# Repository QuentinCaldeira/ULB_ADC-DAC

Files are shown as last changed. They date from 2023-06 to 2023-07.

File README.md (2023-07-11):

# ULB_ADC-DAC

Ce git contient tout les documents liés à la conception de la carte de protection des calculateurs analogiques ADC/DAC.
Dans ce git, vous pouvez trouver :

## Datasheets

Ce répertoire contient toutes les **datasheets** et **notes d'application** qui ont étés utilisées dans la conception dde ce projet.

## Documentation PCB

Ce répertoire contient tout les fichiers de conception du PCB pour le logiciel KiCAD. Des images de la carte et du schematic ont aussi été mis à disposition.

## Gravure

Ce répertoire contient principalement le fichier `.svg` qui à été utilisé pour graver la face avant de la carte, ainsi qu'un template **à l'échelle** pour le gabarit 8x5.

## LaTeX

Ce répertoire contient tout les fichiers liés à la compilation LaTeX du fichier `Documenation.pdf`. Il y a toutes les images liées au document, le template global, les logos, etc...

## Tuto

Ce répertoire contient des tutoriels écrits en `markdown`. Ces tutoriels ont été écrits lorsque j'ai rencontré des difficultés à faire une tâche.

## 3D

Ce répertoire contient les fichiers 3D FreeCAD et `.stl` pour imprimer les pièces permettant de visser la face avant au PCB.

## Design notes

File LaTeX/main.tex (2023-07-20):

\documentclass{report}
\usepackage{quentin}
\definecolor{mycolor}{HTML}{00519d}
\definecolor{darkWhite}{rgb}{0.94,0.94,0.94}
\usepackage{enumitem}
%\usepackage{luacode,numprint,fourier}
\usepackage{hyperref}
\usepackage{pgfplots}
\usepackage{mathtools}
\usepackage{graphicx}
\usepackage{pdfpages}
\usepackage[backend=biber]{biblatex} %backend tells biblatex what you will be using to process the bibliography file
\addbibresource{bib.bib}

\AddToShipoutPicture*{
\begin{tikzpicture}[remember picture, overlay]

\draw[fill=mycolor!50,draw=mycolor!50](current page.north west)rectangle([yshift=-\paperheight/24]current page.north east);
\draw[draw=mycolor!60, line width=1.5mm]([yshift=-\paperheight/24]current page.north west)--([yshift=-\paperheight/24]current page.north east);

\draw[fill=mycolor!50,draw=mycolor!50](current page.south west)rectangle([yshift=\paperheight/24]current page.south east);
\draw[draw=mycolor!60, line width=1.5mm]([yshift=\paperheight/24]current page.south west)--([yshift=\paperheight/24]current page.south east);
\end{tikzpicture}
}

\begin{document}

\titre{
\Huge\textbf{Documentation des cartes de protections}\\[0.2cm]
\large\textbf{Pour le calculateur analogique}\\
\rule{\linewidth}{0.5mm}
\\[2cm]
\LARGE Quentin \textsc{Caldeira}
}

\tableofcontents
\thispagestyle{empty}
\entete
\newpage
\thispagestyle{empty}
\listoffigures
\entete
\listoftables
\entete

\chapter{Contexte}
\thispagestyle{empty}
La carte a pour objectif d'interfacer une face avant avec une carte d'acquisition. Son but est de protéger la carte de potentielles mauvaises manipulations. Étant donné le coût d'une carte d'acquisition, la carte de protection doit protéger la carte d'acquisition. Dans le pire des cas, il est préférable que ce soit la carte de protection qui soit détruite, plutôt que la carte d'acquisition. L'idéal reste qu'aucun des deux éléments ne soit détruit. On souhaite principalement se protéger des courts-circuits et de tensions trop élevées.Une première carte a été réalisée en 1993. Cette carte est fonctionnelle, mais présente quelques défauts qui seront explicités. Cette nouvelle carte a pour objectif de corriger les défauts de l'ancien modèle, de réduire le nombre d'entrées/sorties, et de donner un coup de jeune à la carte.

\chapter{Présentation de l'existant}
\thispagestyle{empty}
Cette partie détaillera les cartes précédemment installées dans le calculateur. La carte dispose de 20 entrées et 12 sorties. Il semblerait qu'elle ait été conçue ainsi afin d'utiliser toutes les broches inférieures du connecteur fond de panier. Le connecteur utilisé est un DIN 41612 de 64 broches. Il s'avère qu'au quotidien, seulement 8 entrées et 2 sorties sont utilisées au maximum. La carte mesure 10 cm de largeur et 22 cm de longueur. C'est une taille standard que toutes les cartes insérées dans les racks doivent respecter. Les connecteurs utilisés sur la face avant sont des connecteurs banane, de couleurs différentes en fonction d'une entrée, d'une sortie ou d'une masse. Il n'y a pas de détrompeur entre les 3 connectiques.

\section{Les cartes d'acquisition}
Les cartes d'acquisition précédemment utilisées étaient des NI PCI 6014 et NI PCI 6024E. Ces cartes sont au format PCI. Les spécifications de cette carte sont synthétisées dans le tableau ci-dessous.

\begin{center}
\begin{table}[h!]
\begin{tabular}{l|l|l|}
\cline{2-3}
                                                                 & Entrée                                 & Sortie                   \\ \hline
\multicolumn{1}{|l|}{Tension d'E/S max en fonctionnement normal} & $\pm 10 V$                             & $\pm 10 V$               \\ \hline
\multicolumn{1}{|l|}{Impédance d'entrée/sortie}                  & 100 G$\Omega$ en parallèle avec 100 pF & 0,1 G$\Omega$            \\ \hline
\multicolumn{1}{|l|}{Protection contre les tensions (On/Off)}    & 25 / 15 V                              & Court-circuit à la masse \\ \hline
\multicolumn{1}{|l|}{Courant de sortie max}                      & -                                      & 5 à 10 mA                \\ \hline
\multicolumn{1}{|l|}{Courant d'entrée max}                       & -                                      & 5 à -10 mA               \\ \hline
\end{tabular}
\caption{Spécifications des cartes PCI 6014 et PCI 6024E}
\end{table}
\end{center}

\section{Alimentation des amplificateurs}
Comme les amplificateurs utilisés sont alimentés en $\pm$15 V, et que les cartes ont une alimentation par défaut de $\pm$24 V, il a fallu adapter cette tension. Des régulateurs de tensions positifs et négatifs ont été utilisés. Un 7815CT a été utilisé pour générer la tension +15 V, et un 7915 pour la tension -15 V. Des capacités de filtrage ont été placés en amont et en aval des alimentations, ainsi que des diodes de protections servant à prévenir des inversions de polarité. La mise en place d'un tel circuit est explicité sur la \bsc{Figure} \ref{fig:alim_exist}. Le choix des capacités se fait souvent en fonction de la documentation du constructeur. De plus, des dissipateurs thermiques ont étés placé afin de limiter la chauffe des régulateurs de tension.

\newpage%%%%%%%%%%%%%%%%%%
\begin{figure}[!h]
\centering
\begin{circuitikz}
\ctikzset{multipoles/thickness=3}
\ctikzset{multipoles/dipchip/width=2}

\draw (0,0) node[dipchip,
num pins=6, hide numbers, no topmark,
external pins width=0](C){7815CT};
\node [right, font=\tiny] at (C.bpin 2) {Vin};
\node [left, font=\tiny] at (C.bpin 5) {Vout};
\draw (C.s)node[above,font=\tiny]{GND} -- ++(0,-1) node[ground]{};

\draw(C.bpin 2)to[empty diode,invert]++(-3,0)node[left]{+24 V};
\draw(C.bpin 2)--++(-.5,0)to[C,l_=22pF]++(0,-2);
\draw(C.bpin 5)--++(.5,0)to[C,l=22pF]++(0,-2)--++(-1.9,0)--++(-1.9,0);
\draw(C.bpin 5)--++(2,0)node[right]{+15 V};

\draw (0,-4) node[dipchip,
num pins=6, hide numbers, no topmark,
external pins width=0](C){7915};
\node [right, font=\tiny] at (C.bpin 2) {Vin};
\node [left, font=\tiny] at (C.bpin 5) {Vout};
\draw (C.s)node[above,font=\tiny]{GND} -- ++(0,-1) node[ground]{};

\draw(C.bpin 2)to[empty diode]++(-3,0)node[left]{-24 V};
\draw(C.bpin 2)--++(-.5,0)to[C,l_=22pF]++(0,-2);
\draw(C.bpin 5)--++(.5,0)to[C,l=22pF]++(0,-2)--++(-1.9,0)--++(-1.9,0);
\draw(C.bpin 5)--++(2,0)node[right]{-15 V};

\end{circuitikz}
\caption{Schéma de principe de protection de l'alimentation sur la carte existante}
\label{fig:alim_exist}
\end{figure}

\section{Protection des entrées}
\subsection{Présentation}

Afin de protéger les entrées, le montage sur la \bsc{Figure} \ref{fig:entree_exist} a été utilisé. Ce montage possède deux diodes Zener en tête-bêche afin d'écrêter la tension à $\pm$10 V. Une résistance de 1 M$\Omega$ est placée en entrée, ainsi qu'en contre-réaction. Une résistance de 1 k$\Omega$ est placée en sortie afin de limiter le courant. Comme la tension de sortie sera de maximum 10 V, le courant devrait être de maximum 10 mA. Le montage est de type \textbf{inverseur}, ce qui veut dire que le gain est d'environ \textbf{-1}. Une entrée à +10 V sera vue comme -10 V par la carte d'acquisition. Ce gain négatif est corrigé par le logiciel qui récupère les signaux (\bsc{MatLAB} en l'occurence). L'amplificateur opérationnel est monté sur un socket DIP-14, afin qu'il soit remplaçable facilement.

\begin{figure}[!h]
\centering
\begin{circuitikz}[european]
\ctikzset{resistors/scale=0.7, capacitors/scale=0.7, diodes/scale=0.7, inductors/scale=0.7}
\draw (0,0) node[op amp,scale=1] (opamp) {};
\draw (opamp.-) --++ (-.5,0)node(b){}--++(0,1)node(a){}to[name=r1,R,l=1M$\Omega$]++(3,0)--++(0,-1.49)node(c){} to (opamp.out);
\draw (a.south)--++(0,1)to[Zener diode]++(1.5,0)to[Zener diode,invert]++(1.5,0)--++(0,-1);
\draw (b.east)to[R,l=1M$\Omega$]++(-2,0)node[left]{Entrée};
\draw (c.west)to[R,l=1k$\Omega$]++(2,0)node[right]{Carte d'acquisition};
\draw (opamp.+)node[ground]{};
\draw (opamp.up) --++ (0,.2) node[above] {15 V};
\draw (opamp.down) --++ (0,-.2) node[below] {-15 V};
\end{circuitikz}
\caption{Schéma de principe de protection des entrées sur la carte existante}
\label{fig:entree_exist}
\end{figure}

\subsection{Mesures}
Pour les entrées, il n'y a pas trop de soucis de protection. En injectant 10 V en entrée, on récupère bien environ -10 V en sortie. Lorsqu'une tension d'alimentation telle que -15 V est injectée, la tension est bien limitée à environ 10 V.

\section{Protection des sorties}
\subsection{Présentation}

Afin de protéger les sorties, le montage sur la \bsc{Figure} \ref{fig:sortie_exist} a été utilisé. Ce montage possède un filtre passe-bas du 1$^{er}$ ordre. L'intérêt d'un tel filtre est discutable, car le signal provient de la carte d'acquisition. Un deuxième filtre passe-bas est placé dans la contre-réaction de l'amplificateur opérationnel. En sortie de ce montage, une résistance de 1 k$\Omega$ a été placée afin de limiter le courant en cas de court-circuits. Cette résistance pose problème car de manière générale, dans un circuit, on cherche à avoir une forte impédance d'entrée et une faible impédance de sortie. On cherche cela afin de faciliter les adaptations d'impédances, c'est-à-dire que la majorité des courants circulant dans un circuit n'ont pas d'impact sur l'autre circuit raccordé. Hors, il a été remarqué qu'avec cette résistance, une chute de tension est observée sur certains procédés.

\begin{figure}[!h]
\centering
\begin{circuitikz}[european]
\ctikzset{resistors/scale=0.7, capacitors/scale=0.7, diodes/scale=0.7, inductors/scale=0.7}
\draw (0,0) node[op amp,scale=1] (opamp) {};
\draw (opamp.-) --++ (-.5,0)node(b){}--++(0,1)node(a){}to[name=r1,R,l=1M$\Omega$]++(3,0)--++(0,-1.49)node(c){} to (opamp.out);
\draw (a.south)--++(0,1)to[C,l=22pF]++(3,0)--++(0,-1);
\draw (b.east)to[R,l=1M$\Omega$]++(-3,0)node[left]{Carte d'acquisition};
\draw (b.west)--++(-0.5,0)--++(0,-0.5)to[C,l=10nF]++(0,-0.5)node[ground]{};
\draw (c.west)to[R,l=1k$\Omega$]++(2,0)node[right]{Sortie};
\draw (opamp.+)node[ground]{};
\draw (opamp.up) --++ (0,.2) node[above] {15 V};
\draw (opamp.down) --++ (0,-.2) node[below] {-15 V};
\end{circuitikz}
\caption{Schéma de principe de protection des sorties sur la carte existante}
\label{fig:sortie_exist}
\end{figure}

\subsection{Mesures}
Pour la sortie, des mesures ont d'abord été faites pour estimer la chute de tension. Sur le procédé de régulation de température par exemple, pour une tension de 10 V fournie par la carte NI, nous ne récupérons que 9 V sur le procédé, soit une chute de 1 V pour 2 mA de consommation. La solution actuelle pour palier à ce problème est de passer par un deuxième amplificateur opérationnel qui a rôle de \textbf{buffer}, c'est-à-dire de faire le lien entre deux étages grâce à sa forte impédance d'entrée et sa faible impédance de sortie. Cependant, cette solution n'est pas viable, car la protection du deuxième amplificateur n'est pas forcément dimensionné pour respecter l'intégrité de la carte.

Lors d'un court-circuit à la masse, le courant est de l'ordre d'une vingtaine de mA, ce qui est tolérable. Cependant, lorsqu'on court-circuite aux alimentations, le courant est de $\pm$ 35 mA, qui est le courant maximal que l'amplificateur peut débiter en court-circuit. Dans ces situations, c'est l'amplificateur qui fait la sécurité et plus le reste du circuit, en fonctionnant en dégradé. Cela peut occasionner une chauffe trop importante et une destruction de l'AOp.

\section{Connecteur fond de panier}
Afin de pouvoir lier les entrées/sorties du PCB à la carte d'acquisition, le PCB dispose d'un connecteur 64 broches qui vient se connecter à une fiche 64 broches placée en fond de rack. Un câble relie ensuite cette fiche à la carte d'acquisition. Les connexions au connecteur 64 broches se faisaient comme sur la \bsc{Figure} \ref{fig:64_old}. On peut voir qu'une ligne sert aux alimentations et une autre sert aux entrées/sorties. 

\begin{figure}[h!]
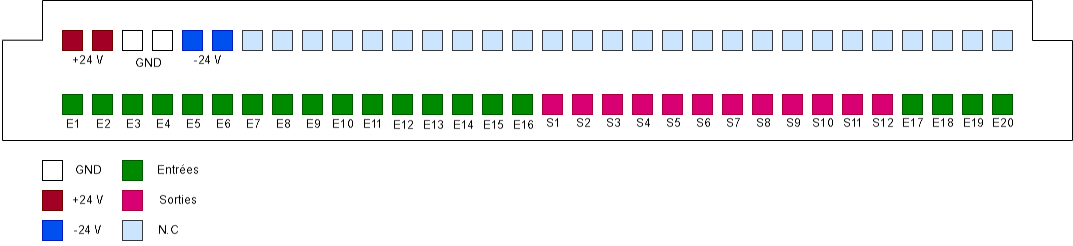
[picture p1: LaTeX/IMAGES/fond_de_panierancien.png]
\begin{center} 
\end{center}
\caption{Connexions entre le PCB et le connecteur 64 broches fond de panier}
\label{fig:64_old}
\end{figure}

\section{La face avant}

La précédente face avant, c'est-à-dire l'interface entre les utilisateurs et la carte, était comme sur la \bsc{Figure} \ref{fig:face_avant_old}.
Cette face avant dispose de 20 entrées analogiques numérotées en jaune, et 8 sorties analogiques numérotées en rouge. Une fiche de masse est mise à disposition pour pouvoir y connecter des appareils de mesures. La face avant dispose de quatre vis permettant de la fixer au support, et deux vis supplémentaires permettant de fixer la face avant au PCB. Toutes les entrées sorties sont des fiches banane. Ces fiches banane sont ensuite reliées à l'intérieur de la carte par des \textbf{câbles}, soudés aux différents points des entrées/sorties. Cette liaison est montrée dans la \bsc{Figure} \ref{fig:liaison_pcb_old}.
\bigbreak
\begin{minipage}{0.45\textwidth}
\centering
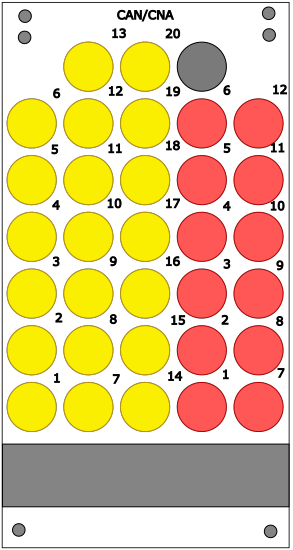
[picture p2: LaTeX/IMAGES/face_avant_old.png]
 

\captionof{figure}{Face avant de l'ancienne carte}
\label{fig:face_avant_old}
\end{minipage}
\hfill
\begin{minipage}{0.45\textwidth}
\centering
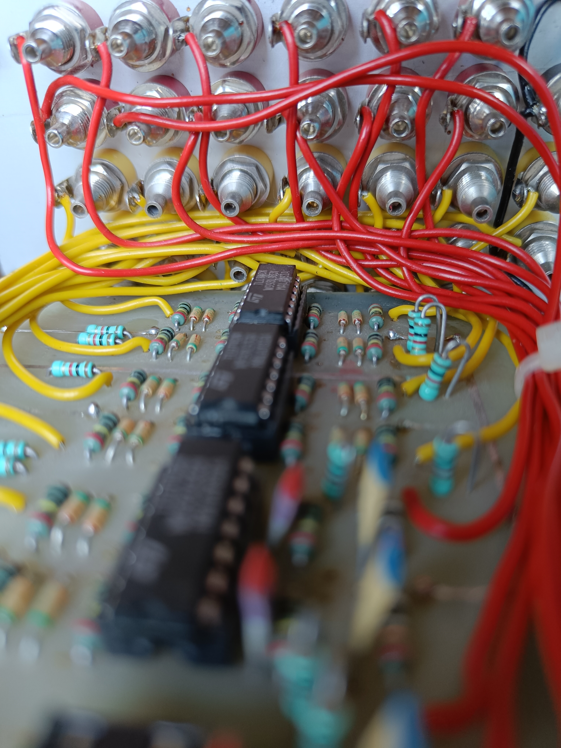
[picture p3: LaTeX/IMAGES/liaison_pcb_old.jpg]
 

\captionof{figure}{Connexion des fiches bananes au PCB}
\label{fig:liaison_pcb_old}
\end{minipage}

\chapter{Contraintes de la nouvelle carte}
\thispagestyle{empty}

Maintenant que l'existant est plus claire, il faut dresser un cahier des charges qui permettra de dimensionner les nouveaux éléments de la carte. Il est à noter que le laboratoire a décidé de faire évoluer ses cartes d'acquisitions, abandonnant le format PCI pour le format PCIe. Les nouvelles cartes seront des NI PCIe 6321 et NI PCIe 6323. Il faudra donc dimensionner le circuit pour respecter les contraintes de ces nouvelles cartes.

\section{Etude des nouvelles cartes d'acquisitions}
Les nouvelles cartes étant différentes, il faut prêter attention à leurs spécifications. Ces dernières sont synthétisées dans le tableau ci-dessous.

\begin{table}[!h]
\begin{center}
\begin{tabular}{l|l|l|}
\cline{2-3}
                                                                 & Entrée                                & Sortie       \\ \hline
\multicolumn{1}{|l|}{Tension d'E/S max en fonctionnement normal} & $\pm 11 V$                            & $\pm 10 V$   \\ \hline
\multicolumn{1}{|l|}{Impédance d'entrée/sortie}                  & 10 G$\Omega$ en parallèle avec 100 pF & 0,2 $\Omega$ \\ \hline
\multicolumn{1}{|l|}{Protection contre les tensions (On/Off)}    & $\pm$25 / 15 V                        & $\pm$ 15 V   \\ \hline
\multicolumn{1}{|l|}{Courant de sortie max}                      & -                                     & 5 mA         \\ \hline
\multicolumn{1}{|l|}{Courant d'entrée max}                       & $\pm$ 20 mA pendant une surtension    & 5 mA         \\ \hline
\multicolumn{1}{|l|}{Courant de court-circuit}                   & -                                     & $\pm$ 15 mA  \\ \hline
\end{tabular}
\caption{Spécifications des cartes PCIe 6321 et PCIe 6323}
\end{center}
\end{table}

\section{Ajouts par rapport à l'ancienne version}
\subsection{Réduction du nombre d'E/S}
Il s'avère que la carte précédente a été surdimensionnée à l'époque. En effet, sur les 20 entrées présentes, seulement huit sont utilisées au maximum simultanément. Il en va de même pour les sorties, seulement deux sont utilisées au maximum simultanément. Une réduction du nombre d'entrées/sorties permettra un gain de place sur la carte, mais facilitera aussi l'ajout de nouvelles fonctionnalités. Il est à noté que les nouvelles cartes partagent la même disposition que les anciennes en ce qui concerne les entrées/sorties analogiques. Il n'y aura donc pas de modifications à apporter à ce sujet.

\subsection{PWM}
Le laboratoire à pour volonté de vouloir ajouter deux sorties PWM par carte, afin de pouvoir piloter des procédés. Il faudra veiller à protéger efficacement cette sortie PWM, comme les sorties analogiques, en cas de mauvais branchement.

\subsection{Encodeur}
Le laboratoire souhaite aussi ajouter deux entrées d'encodeur par carte, afin de pouvoir acquérir la position des moteurs sur des procédés. Il faudra veiller à protéger efficacement cette entrée d'encodeur, comme les entrées analogiques, en cas de mauvais branchement.

\section{Cahier des charges}
\subsection{Dimensions}
La carte devra être aux dimensions du rack de laboratoire, c'est à dire 22 cm de longueur pour 10 cm de largeur maximum.

\subsection{Protection des entrées analogiques}
Les entrées seront manipulées par les élèves. Il faut que ces entrées soient :
\begin{itemize}
\item De couleur différente par rapport aux sorties, PWM et encodeurs
\item Munies de prises bananes pour accueillir les câbles mis à disposition dans le laboratoire
\item Au nombre de 8 par carte
\item Protégées de sorte à ce que la tension arrivant à la carte ne dépasse pas $\pm$ 10 V
\item Protégées de sorte à ce que le courant arrivant à la carte ne dépasse pas $\pm$ 20 mA
\item Facilement réparable, c'est-à-dire qu'un composant griller soit facilement remplaçable
\item De gain le plus proche de 1, c'est-à-dire que le signal émis en entrée doit être le même que celui reçu par la carte, dans un fonctionnement normal
\end{itemize}

\subsection{Protection des sorties analogiques}
Les sorties seront manipulées par les élèves. Il faut que ces sorties soient :
\begin{itemize}
\item De couleur différente par rapport aux entrées, PWM et encodeurs
\item Munies de prises bananes pour accueillir les câbles mis à disposition dans le laboratoire
\item Au nombre de 2 par carte
\item Protégées de sorte à ce que la tension arrivant à la carte ne dépasse pas $\pm$ 15 V
\item Protégées de sorte à ce que le courant sortant de la carte ne dépasse pas $\pm$ 5 mA
\item Facilement réparable, c'est-à-dire qu'un composant griller soit facilement remplaçable
\item De gain le plus proche de 1, c'est-à-dire que le signal émis par la carte doit être le même que celui reçu, dans un fonctionnement normal
\item Avoir une impédance de sortie faible pour permettre une meilleure adaptation d'impédance avec les différentes charges du laboratoire
\end{itemize}

\chapter{Etude des nouvelles protections}
\thispagestyle{empty}
\section{Protection des entrées}
\subsection{Veille technologique}
Dans un premier temps, il est intéressant de se renseigner sur différentes méthodes de protection des entrées. On souhaite principalement se protéger d'une tension d'entrée qui sera trop grande. Une solution simple serait de mettre des diodes Zener en tête-bêche, comme l'illustre parfaitement ce site de l'Université du Mans \cite{Rousseau}. On peut, en choisissant la tension de claquage de la diode, écrêté la tension positive et négative. Cette solution à tout de même une limite. Une résistance est placée en amont pour limiter le courant circulant dans les diodes. Si ce courant devient trop fort, la puissance que la diode devra dissiper deviendra trop élevée et elle sera détruite. Il faut donc correctement dimensionner les diodes et la résistance, en fonction de la tension maximale qu'on risque d'avoir en entrée.

Une autre solution, en utilisant aussi des composants passifs, est de faire comme un pont de résistance et de condensateurs. Cette solution est démontrée dans cet article \cite{FilipovaPetrakieva2020}. Cette solution permet de protéger le circuit contre des surtensions. Même si c'est intéressant de pouvoir s'en protéger, ce circuit sert principalement à protéger des surtensions momentanées et non continue. De ce fait, il ne semble pas adapter à l'application.

Il a aussi été envisagée d'utiliser un \verb+LT4363+ \cite{LT4363AD}, qui est un circuit intégré de Analog Devices permettant de couper le circuit en cas de surtensions, et dispose d'une limitation de courant. Ce composant aurait pu être utilisé mais il est bien trop onéreux pour l'application. Étant donné qu'environ vingt cartes seront fabriquées, mettre un composant à plus d'une dizaine d'euros par entrée analogique n'était pas envisageable, et sûrement surdimensionné pour l'application.

Si on regarde du côté des protections mises sur les microcontroleurs, ce qui peut s'apparenter à une carte d'acquisition avec des niveaux de tension moindre, les solutions semblent toujours être les mêmes. Le site de Digikey \cite{digikey} montre de nombreuses solutions utilisées au quotidien. La première est une simple résistance qui permet de limiter le courant en entrée. Il faut que cette résistance reste négligeable par rapport à l'impédance d'entrée de la carte, qui est de l'ordre du Gigaohm. Une autre solution est d'utiliser des diodes de \textbf{clamping}, qui permettent d'écrêter la tension avant d'aller à la carte, comme précédemment.

Comme dans l'ancienne carte, des amplificateurs opérationnels peuvent être utilisés pour faire un \textbf{buffer}, permettant une bonne adaptation d'impédance et une sorte de \textbf{fusible} artificiel, qui pourrait séparer les deux parties du circuit s'il est détruit. Le séparation n'est pas sûre à 100$\%$, car on ne sait pas comment le composant se comportera en état dégradé, et qu'elles sont les jonctions qui seront crées. Mais, de manière générale, on peut espérer une isolation entre les deux parties.

\subsection{Solution retenue}
Afin de protéger les entrées, le montage sur la \bsc{Figure} \ref{fig:entree_new} a été utilisé. Ce montage possède deux diodes Zener en tête-bêche afin d'écrêter la tension à $\pm$10 V. La saturation de l'amplificateur ne suffira pas à écrêter, car elle dépasse $\pm$10 V. Une résistance de 12 k$\Omega$ est placée en entrée afin de limiter le courant circulant dans les diodes. Un condensateur de 1 nF est placé pour faire un filtre passe-bas. Ce condensateur n'est pas obligatoire et sera retiré pour le moment. Le filtre n'a pas pour volonté d'agir comme un \textbf{filtre anti-repliement}, une carte est déjà prévue à cet effet. Ce filtre a été placé pour nettoyer le signal d'entrée. Une résistance de 150 k$\Omega$ est placée en sortie afin de limiter le courant. Comme la tension de sortie sera de maximum 10 V, le courant devrait être de maximum 10 mA. Il n'y aura donc pas d'inversion de tension à corriger. L'amplificateur opérationnel est monté sur un socket DIP-14, afin qu'il soit remplaçable facilement. Il n'y a pas vraiment de critères de choix pour l'amplificateur. Etant donné que nous sommes sur un montage de type buffer, avec une application plutôt basse fréquence, n'importe lequel ferait l'affaire. Des TL064CN ont donc étés utilisés, afin d'harmoniser les stocks d'amplificateurs avec les cartes de filtres anti-repliement.

\newpage

\begin{figure}[!h]
\centering
\begin{circuitikz}[european]
\shorthandon{;:!?}
\ctikzset{resistors/scale=0.7, capacitors/scale=0.7, diodes/scale=0.7, inductors/scale=0.7}
\draw (0,0) node[op amp,scale=1] (opamp) {};
\draw (opamp.-) --++ (-.5,0)node(b){}--++(0,1)node(a){}--++(3,0)--++(0,-1.49)node(c){} to (opamp.out);
%\draw (a.south)--++(0,1)to[Zener diode]++(1.5,0)to[Zener diode,invert]++(1.5,0)--++(0,-1);
\draw (opamp.+)--++(-2,0)node(zener){}--++(-2,0)node(capa){}to[R,l=12 k$\Omega$]++(-2,0)node[left]{Entrée};
%\draw (b.east)to[R,l=12 k$\Omega$]++(-4,0)node[left]{Entrée};
\draw(capa.east)to[C,l=1 nF]++(0,-2)node[ground]{};
\draw(zener.east)to[Zener diode,l=10 V]++(0,-1)to[Zener diode,invert, l= 10 V]++(0,-1)node[ground]{};

\draw (c.west)to[R,l=150 k$\Omega$]++(2,0)node[right]{Carte d'acquisition};
\draw (opamp.up) --++ (0,.2) node[above] {15 V};
\draw (opamp.down) --++ (0,-.2) node[below] {-15 V};
\end{circuitikz}
\shorthandoff{;:!?}
\caption{Schéma de principe de protection des entrées sur la nouvelle carte}
\label{fig:entree_new}
\end{figure}

\section{Protection des sorties}
\subsection{Veille technologique}
Dans un premier temps, il faut se renseigner sur les méthodes existantes permettant de protéger une sortie. On cherche principalement une protection afin d'empêcher les élèves de détruire la carte en faisant des courts-circuits. Une première solution simple serait d'utiliser des détrompeurs, pour que l'élève ne puisse connecter le câble qu'aux éléments souhaités. Cependant, cette solution n'est pas envisageable car le laboratoire souhaite conserver les fiches bananes pour les manipulations des élèves.
Il est à noter que le calculateur dispose déjà d'un circuit de détection des courts-circuits, pour le bloc d'alimentation uniquement, qui émet un signal sonore et/ou lumineux. Il n'arrête cependant pas le système. Pour rappel le problème actuel est que la résistance utilisée crée une chute de potentiel, par problème d'adaptation d'impédance \cite{Gabriel2012}. Une autre solution pourrait être de trouver une valeur de résistance permettant de limiter le courant à la valeur souhaitée tout en minimisant la chute de tension. Cette solution est envisageable mais difficile à mettre en œuvre car chaque procédé à sa propre impédance d'entrée. Comme on cherche à faire une carte indépendante du procédé, c'est plus compliqué.
Une autre solution est de limiter le courant que peut sortir l'amplificateur opérationnel par ses alimentations. En limitant le courant entrant par les alimentations, on pourra limiter le courant sortant en court-circuit et donc la chauffe du composant. Ce type de montage est montrer sur la note d'application de Texas Instruments \cite{appnoteti}.
En tout cas, il est préférable de continuer à utiliser des amplificateurs opérationnel entre la sortie de la carte d'acquisition et les procédés, comme buffer.

\subsection{Solution retenue}
Afin de protéger les sorties, le montage sur la \bsc{Figure} \ref{fig:sorties_new} a été utilisé. Afin de contrer le problème de la chute de tension liée à une impédance de sortie trop forte du montage, l'idée a été de brider l'amplificateur sur les alimentations. Comme il est souhaitable que le courant en cas de court-circuit soit le plus petit possible, si on limite le courant sur les alimentations, le courant sera limité en court-circuit. Cette limite doit être calculée pour que le circuit puisse tout de même débiter assez de courant pour les procédés. Une résistance de 2 k$\Omega$ est placée en sortie de l'AOp, en amont de la contre-réaction, afin d'aider à limiter le courant. L'AOp est en montage \textbf{non-inverseur}, ce qui veut dire que le gain est d'environ \textbf{1}. Pour chacune des alimentations, il y a d'abord une résistance de 2 k$\Omega$ qui permet de limiter le courant entrant dans l'amplificateur, une capacité de 10 nF en parallèle afin de filtrer l'alimentation, et une diode Zener de 15 V pour aider à contrer les chutes de tensions. En effet, comme le courant absorber est parfois important, la résistance crée une chute de tension trop importante qui va faire saturer l'amplificateur trop vite, donc une diode Zener a été placée en parallèle pour aider à maintenir 15 V dans ces cas-là. Une capacité de 0.1 $\mu$F a été placée entre l'amplificateur et la masse, conformément à la note d'application de Texas Instrument dont est grandement inspiré ce montage. Cette note sera disponible en Annexe. L'amplificateur sera une fois de plus monté sur un socket DIP-14 afin de pouvoir le remplacer facilement. L'amplificateur sera le même que pour la partie entrée, un TL064CN. Il faudra veiller à surdimensionner les résistances en termes de dissipations de puissance, car comme elles brident l'alimentation, elles dissipent beaucoup en chaleur.

\newpage%%%%%%%%
\begin{figure}[!h]
\centering
\begin{circuitikz}[european]
\shorthandon{;:!?}
\ctikzset{resistors/scale=0.7, capacitors/scale=0.7, diodes/scale=0.7, inductors/scale=0.7}
\draw (0,0) node[op amp,scale=1] (opamp) {};
%\draw (opamp.-) --++ (-.5,0)node(b){}--++(0,1)node(a){}--++(5,0)--++(0,-1.49)node(c){}to [R,l=2 k$\Omega$]++(-2,0) to (opamp.out);%%CR-

\draw (opamp.-) --++ (-.5,0)node(b){}--++(0,1)node(a){}to[crossing]++(3.215,0)--++(1.785,0)--++(0,-1.49)node(c){}to [R,l=1 k$\Omega$]++(-2,0) to (opamp.out);%%CR-
\draw (opamp.+)--++(-2,0)node[left]{Carte d'acquisition};

\draw (c.west)--++(1,0)node[right]{Sortie};

%\draw (opamp.up) --++ (0,.2) node[above] {15 V};
\draw (opamp.up) --++ (0,2) node(anch+){};
\draw(anch+.center)to[C,l=0.1 uF]++(2,0)node[ground]{};
\draw(anch+.center)--++(0,1)node(bul){$\bullet$}--++(-2,0)to[Zener diode, l=15 V, invert]++(0,2)--++(2,0)to[R,l=2 k$\Omega$]++(0,-2)--++(2,0)to[C,l_=10 nF]++(0,2)--++(-2,0)--++(0,.2)node[above]{15 V};
\draw (opamp.down) --++ (0,-1) node(anch-){};
\draw(anch-.center)to[C,l=0.1 uF]++(-2,0)node[ground]{};
\draw(anch-.center)--++(0,-1)node(bul){$\bullet$}--++(-2,0)to[Zener diode, l_=15 V]++(0,-2)--++(2,0)to[R,l_=2 k$\Omega$]++(0,2)--++(2,0)to[C,l=10 nF]++(0,-2)--++(-2,0)--++(0,-.2)node[below]{-15 V};
\end{circuitikz}
\shorthandoff{;:!?}
\caption{Schéma de principe de protection des sorties sur la nouvelle carte}
\label{fig:sorties_new}
\end{figure}

\section{Alimentation du circuit}
Pour alimenter le montage, l'alimentation principale sera celle des racks, c'est-à-dire $\pm$24\~V. Les amplificateurs seront eux alimentés en $\pm$15\~V, à l'aide de deux régulateurs de tensions : le 7815CV et le 7915CV. Le montage sera équivalent à celui de la précédente carte, comme le montre la \bsc{Figure} \ref{fig:alim_new}. Les diodes sont des 1N4001.

\begin{figure}[!h]
\centering
\shorthandon{;:!?}
\begin{circuitikz}
\ctikzset{multipoles/thickness=3}
\ctikzset{multipoles/dipchip/width=2}

\draw (0,0) node[dipchip,
num pins=6, hide numbers, no topmark,
external pins width=0](C){7815CV};
\node [right, font=\tiny] at (C.bpin 2) {Vin};
\node [left, font=\tiny] at (C.bpin 5) {Vout};
\draw (C.s)node[above,font=\tiny]{GND} -- ++(0,-1) node[ground]{};

\draw(C.bpin 2)to[empty diode,invert]++(-3,0)node[left]{+24 V};
\draw(C.bpin 2)--++(-.5,0)to[C]++(0,-2);
\draw(C.bpin 5)--++(.5,0)to[C]++(0,-2)--++(-1.9,0)--++(-1.9,0);
\draw(C.bpin 5)--++(2,0)node[right]{+15 V};

\draw (0,-4) node[dipchip,
num pins=6, hide numbers, no topmark,
external pins width=0](C){7915CV};
\node [right, font=\tiny] at (C.bpin 2) {Vin};
\node [left, font=\tiny] at (C.bpin 5) {Vout};
\draw (C.s)node[above,font=\tiny]{GND} -- ++(0,-1) node[ground]{};

\draw(C.bpin 2)to[empty diode]++(-3,0)node[left]{-24 V};
\draw(C.bpin 2)--++(-.5,0)to[C]++(0,-2);
\draw(C.bpin 5)--++(.5,0)to[C]++(0,-2)--++(-1.9,0)--++(-1.9,0);
\draw(C.bpin 5)--++(2,0)node[right]{-15 V};

\end{circuitikz}
\shorthandoff{;:!?}
\caption{Schéma de principe de protection de l'alimentation sur la nouvelle carte}
\label{fig:alim_new}
\end{figure}

\chapter{Intégration des protections dans le calculateur}
\thispagestyle{empty}
\section{Connecteur fond de panier}
Pour les entrées/sorties analogiques, les anciennes et nouvelles cartes d'acquisition n'ont pas changé de disposition des pins. De ce fait, la disposition faite sur la précédente carte de protection pourra être conservée sans avoir à refaire le câble liant le fond de panier à la carte d'acquisition. Les branchements au connecteur fond de panier se feront tel que sur la \bsc{Figure} \ref{fig:64_new}. 

\begin{figure}[h!]
\begin{center}
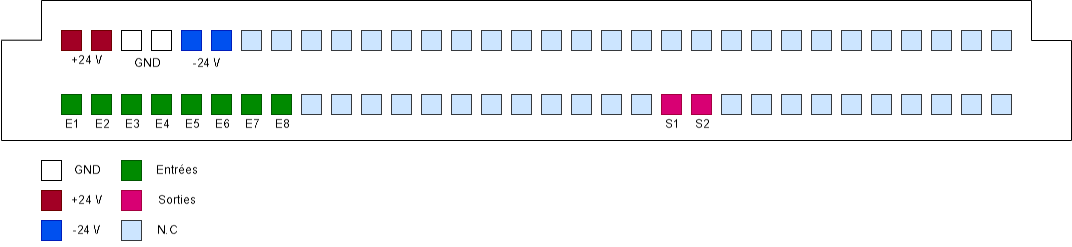
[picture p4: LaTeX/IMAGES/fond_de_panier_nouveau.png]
 
\end{center}
\caption{Connexions entre le PCB et le connecteur 64 broches fond de panier}
\label{fig:64_new}
\end{figure}

Il est important de ramener les pins non-connectés à la masse, car par défaut la carte fonctionne en mode différentiel. Elle fait donc la différence entre les pins A0 et A8, A1 et A9, etc... Les pattes A8, A9, 10, [...], A15 sont sur les pins non connectés. Le potentiel est donc flottant et la mesure différentielle n'est pas bonne. Il faut donc soit connecté ces pins à la masse, soit faire fonctionner la carte d'acquisition en \textbf{single-ended}, ou encore les deux solutions en même temps. Pour notre part, les pins seront connectés à la masse.

\section{La face avant}
Pour concevoir la nouvelle face avant, on utilise des fiches bananes avec des couleurs différentes en fonction d'une entrée, d'une sortie ou d'une masse. Etant donné que le nombre d'entrées/sorties est moindre, il est intéressant de prendre plus de place sur la face avant afin de mettre des indications visibles et lisibles pour les étudiants. Par ailleurs, sur une face avant, nous pouvons disposer au maximum 8 fiches en longueur et 5 fiches en largeur. Nous n'utiliserons que 4 fiches maximum en largeur, pour que la fixation du PCB à la face avant se fasse de manière plus simple. En temps normal, il faut impérativement que le PCB passe entre deux fiches de la face avant, ce qui est contraignant. Ces quatre idées, visibles sur la \bsc{Figure} \ref{fig:design_face_avant} ont étés proposées aux utilisateurs des calculateurs analogiques.
\newpage
\begin{figure}[!h]
\begin{center}
 
\caption{Différentes idées de face avant}
\label{fig:design_face_avant}
\end{center}
\end{figure}

La face avant qui a été retenue est la deuxième, avec un texte plutôt centré au milieu. Le fichier pour la gravure à été mis à disposition dans le répertoire \verb+ Gravure/face_avant_v1.svg+. Il y a aussi un fichier guide, où les côtes du gabarit présentant 8x5 connecteurs ont étés reportées. Ce fichier peut être utile pour concevoir de nouvelles faces avant. Les paramètres utilisés pour la gravure ont étés :
\begin{itemize}
\item Résolution : 600 dpi
\item Vitesse : 30$\%$
\item Puissance : 50$\%$
\end{itemize}

La gravure a été effectuée sur le côté non protégé des plaques d'aluminium. Il faut bien veiller à placer son dessin en haut à gauche de la feuille sur Inkscape, pour effectuer la gravure. En effet, il y a une équerre dans les graveuses qui permet de positionner la plaque d'aluminium.

\chapter{Design du PCB}
\thispagestyle{empty}
\section{Design}
Pour faire le PCB, le logiciel KiCAD à été utilisé. Le PCB à ensuite été fabriqué par JLCPCB. Les fichiers de conceptions, la liste des composants, ainsi que des copies \verb+pdf+ et \verb+png+ sont disponibles dans le répertoire \verb+PCB+. Un emplacement à été laisser libre pour les condensateurs de filtrage sur le circuit de protection des entrées. De ce fait, une capacité pourra être rajoutée a besoin. Un emplacement pour une résistance additionnelle a été placée en parallèle des résistance de protection des sorties, afin de faire varier sa valeur au besoin. La résistance actuelle à été dimensionnée pour les procédés actuellement utilisés. Si jamais une chute de tension est observé sur de nouveaux procédés, il faudra faire chuter la valeur de cette résistance. Il faut tout de même veiller à ce que les mesures en court-circuit avec cette résistance soit dans une gamme de valeurs non destructive pour la carte, c'est-à-dire inférieur à 35 mA. Des vias ont étés ajoutés pour venir y souder les fils qui relieront la carte à la face avant. Les deux faces sont utilisés, notamment à cause de l'alimentation de la carte qui bloque l'accès à certaines entrées. Un plan de masse à été fait sur la face du dessous pour faciliter le routage.

\section{Problèmes rencontrés}

Un problème rencontré lorsqu'on passe commande auprès de JLCPCB avec un PCB fait sur KiCAD est qu'après lui avoir donner le fichier de placement des composants, les composants sont mal placés sur le PCB. Cela est dû à un problème de normes entre KiCAD et JLCPCB sur certaines empreintes. Une première solution est d'utiliser le logiciel EasyEDA qui fonctionne de paire avec JLCPCB. Une autre solution, qui a été utilisée ici, est un plugin Python du nom de JLC2KiCad. Ce plugin permet de générer des empreintes, symboles et modèles 3D à partir du numéro de référence JLCPCB. Une fiche explicative est disponible dans le répertoire \verb+Tuto+. Avec cette méthode, toutes les empreintes correspondront parfaitement aux composant souhaités.\\

La carte n'a pas été fabriquée aux bonnes dimensions (20 cm par 10 cm au lieu de 22 cm par 10 cm). De ce fait, des extensions plastiques faites à l'imprimante 3d ont été crées afin que la carte rentre parfaitement dans les racks. Les fichiers de conception 3d sont disponibles sur GitHub. La pièce à été conçue sur FreeCAD, un logiciel  open-source.\\

Le dernier soucis rencontré est l'implémentation des vias sur la carte. Des vias ont étés placés pour venir y souder des fils reliant la face avant à la carte. Le problème est que le fabricant ne met pas de pastille de cuivre autour si on met un via sur KiCAD. Les câbles ont donc étés soudés à l'intérieur du via, mais l'opération  est plus compliquée. La connexion se fait tout de même sans problèmes.

\chapter{Caractérisation de la carte}
\thispagestyle{empty}
Les cartes ont étés caractérisées en fréquence et en phase, et les courants en court-circuits ont étés relevés.
\section{Caractérisation des entrées}
Pour caractériser les entrées, un signal sinusoïdal d'amplitude $\pm$5 V à été injecté, et la sortie mesurée à l'oscilloscope.  La réponse en amplitude est visible \bsc{Figure} \ref{fig:ampin} et celle en phase \bsc{Figure} \ref{fig:phiin}.

\begin{figure}[h!]
\begin{center}
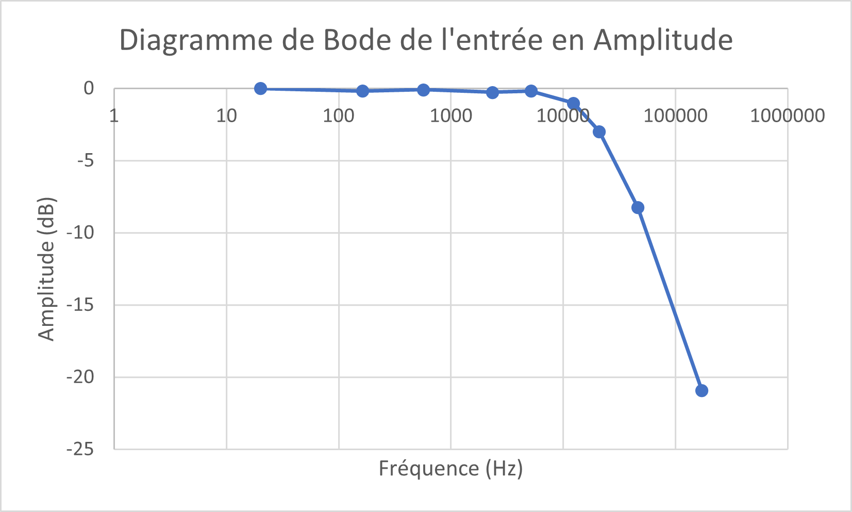
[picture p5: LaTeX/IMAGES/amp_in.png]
 
\end{center}
\caption{Diagramme de Bode en amplitude des entrées}
\label{fig:ampin}
\end{figure}

\begin{figure}[h!]
\begin{center}
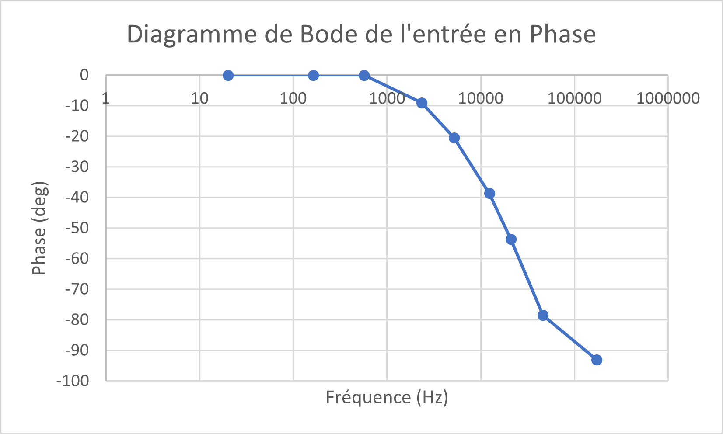
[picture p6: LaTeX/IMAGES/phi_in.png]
 
\end{center}
\caption{Diagramme de Bode en phase des entrées}
\label{fig:phiin}
\end{figure}

\section{Caractérisation des sorties}
Pour caractériser les sorties, un signal sinusoïdal d'amplitude $\pm$5 V à été injecté, et la sortie mesurée à l'oscilloscope.  La réponse en amplitude est visible \bsc{Figure} \ref{fig:ampout} et celle en phase \bsc{Figure} \ref{fig:phiout}.

\begin{figure}[h!]
\begin{center}
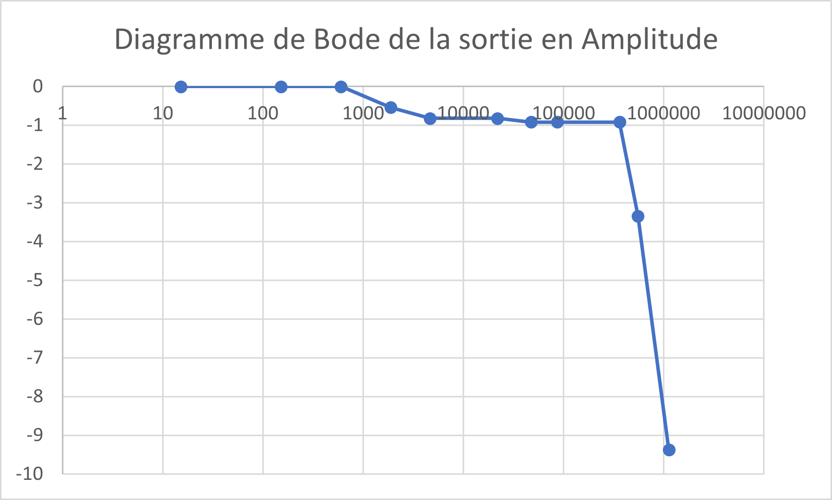
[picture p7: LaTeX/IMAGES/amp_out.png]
 
\end{center}
\caption{Diagramme de Bode en amplitude des sorties}
\label{fig:ampout}
\end{figure}

\begin{figure}[h!]
\begin{center}
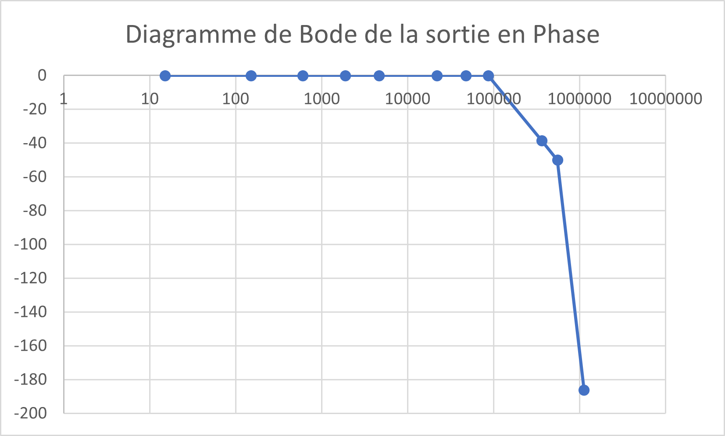
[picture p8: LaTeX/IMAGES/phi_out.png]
 
\end{center}
\caption{Diagramme de Bode en phase des sorties}
\label{fig:phiout}
\end{figure}

\thispagestyle{empty}
\printbibliography
\thispagestyle{empty}

\end{document}

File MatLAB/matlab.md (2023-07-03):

# Contraintes Data Acquisition Toolbox et NI PCIe 6323

## Spécifications de la carte NI PCIe 6323

### Entrées analogiques

- Sample Rate maximal de 250 kS/s
- Taille de la mémoire FIFO de 4095 échantillons
- Transfert de données DMA

### Sorties analogiques

- Sample Rate de 900 kS/s maximum si une sortie active
- Sample Rate de 840 kS/s maximum si deux sorties actives
- Sample Rate de 775 kS/s maximum si trois sorties actives
- Sample Rate de 719 kS/s maximum si quatre sorties actives
- Taille de la mémoire FIFO de 8191 échantillons répartis entre les quatre sorties
- Transfert de données DMA

## Fonctions utilisées de la Data Acquisition Toolbox

- `daq` qui permet de créer un objet DataAcquisition
- `addinput` qui permet d'ajouter des entrées
- `addoutput` qui permet d'ajouter ddes sorties
- `start` qui permet de lancer une acquisition en arrière plan
- `read` qui permet de récupérer les données acquises
- `flush` qui permet de vider les buffers

## Test réalisé

Pour tester la carte, on génère un signal PWM continu sur `ctr0`, le pin 2 de la carte. On connecte un bouton poussoir sur `ai3`, le pin 30 de la carte. On visualise le signal PWM généré à l'oscilloscope. On souhaite avoir un signal PWM avec un rapport cyclique de 0,2. Si le bouton est enclenché, le rapport cyclique passe a 0,8.

## Observations et explications

- Le signal PWM est correctement généré. Sa fréquence peut montée à 100 kHz sans problèmes
- La détection du bouton ne se fait pas correctement. Il s'avère que le SampleRate par défaut est de 1000 échantillons par seconde, ce qui fais une période de 1 ms. Hors, le temps d'exécution de la fonction `read` pour receuillir un échantillons est supérieur à 1 ms. La mise à jour des échantillons n'est donc pas perçue par le programme.
- Un SampleRate plus faible permet de détecter l'actualisation du bouton. Il faut que la mise à jour des échantillons soit plus rapide que le temps d'exécution de la lecture
- Lire un plus gros paquet d'échantillons permet une meilleure détection. En effet, la carte stocke 4095 données puis les envoi au PC. En faisant une lecture simple, on lui demande de faire un transfert pour seulement 1 échantillon. 

## Solutions envisagées

- Réduire le SampleRate pour atteindre des temps inférieur au temps d'exécution de la fonction `read`. Le problème est qu'il ne sera pas possible d'agir rapidement sur un procédé (temps de réaction facilement supérieur à la dizaine voir centaine de ms)
- Prendre plus d'échantillons et les moyenner. L'acquisition se fera plus rapidement. Le problème est que ça rajoute du temps de processing des données après l'acquisition, et perte de précision de la mesure en faisant un moyennage sur plusieurs échantillons
- Trouver une fonction plus **bas-niveau** afin de gagner en temps d'exécution sur la lecture d'un échantillon. Cela permettra de pouvoir augmenter le SampleRate.

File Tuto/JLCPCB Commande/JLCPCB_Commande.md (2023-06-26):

# Tutoriel pour commander sur JLCPCB avec un PCB KiCAD (FR)

## Fichiers KiCAD
### Fichiers de fabrication
Pour fabriquer le PCB sur JLCPCB, il faut créer des fichiers Gerber `.gbr` pour les couches que l'on souhaite créer. Pour se faire, dans l'éditeur de PCB KiCAD, il faut cliquer sur *Fichier>Fichiers de Fabrication>Gerbers* comme sur la figure ci-dessous.

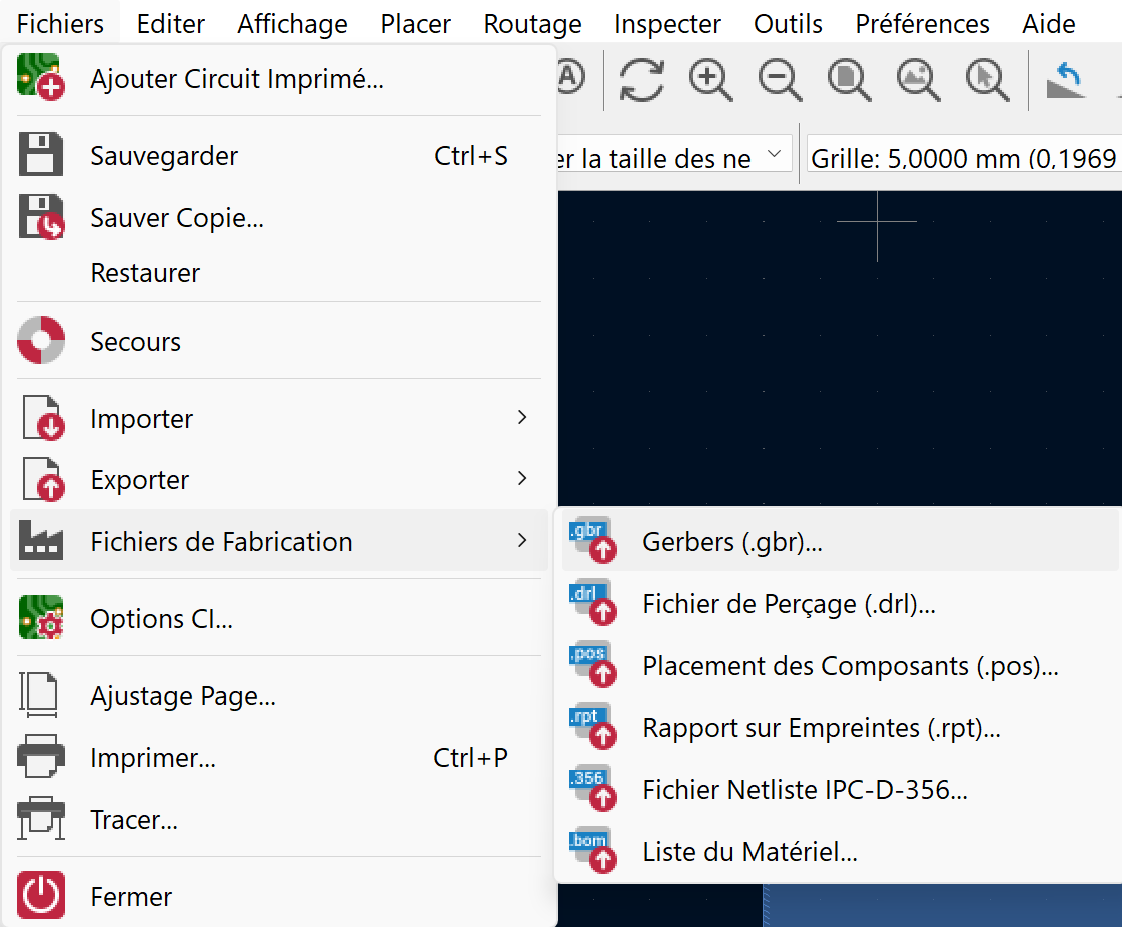
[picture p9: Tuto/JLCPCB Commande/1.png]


Une fenêtre s'ouvre, sur laquelle on peut notamment choisir les couches à créer. Il faut impérativement conserver les couches 

- F.Cu, c'est la couche cuivre supérieure
- B.Cu, c'est la couche de cuivre inférieure
- F.Silkscreen, c'est la sérigraphie supérieure
- B.Silkscreen, c'est la sérigraphie inférieure
- F.Mask, c'est le masque de soudure supérieur
- B.Mask, c'est la masque de soudure inférieur
- Edge.Cuts, pour avoir les bordures de la carte
  
On peut en soit mettre toutes les couches par sécurité, mais certaines ne sont pas nécessaires comme User.Eco1 par exemple. Il ne faut surtout pas oublier les couches de masque sinon le fabricant ne pourra pas produire la carte

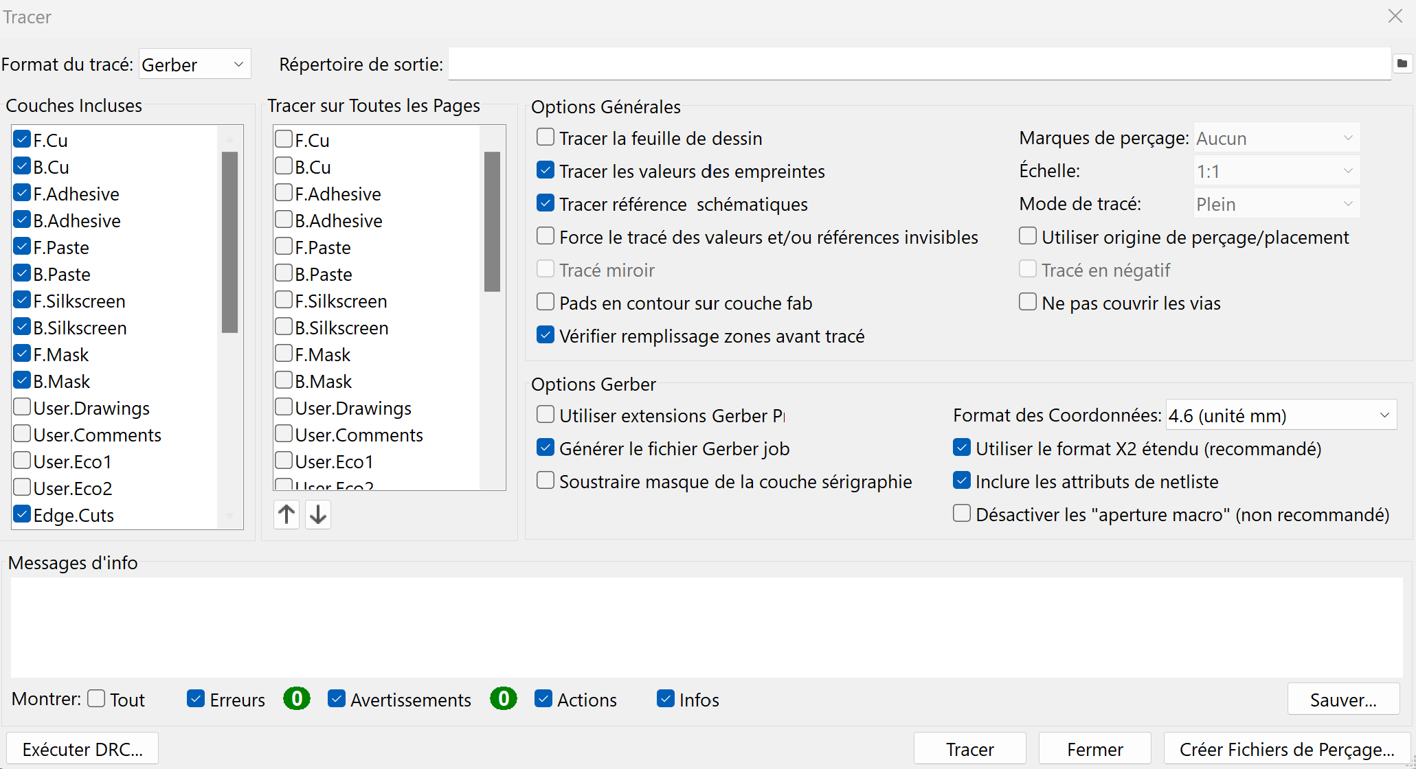
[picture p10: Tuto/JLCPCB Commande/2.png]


On clique ensuite sur tracer, puis on peut créer les fichiers de perçage par la même occasion (en bas à droite).

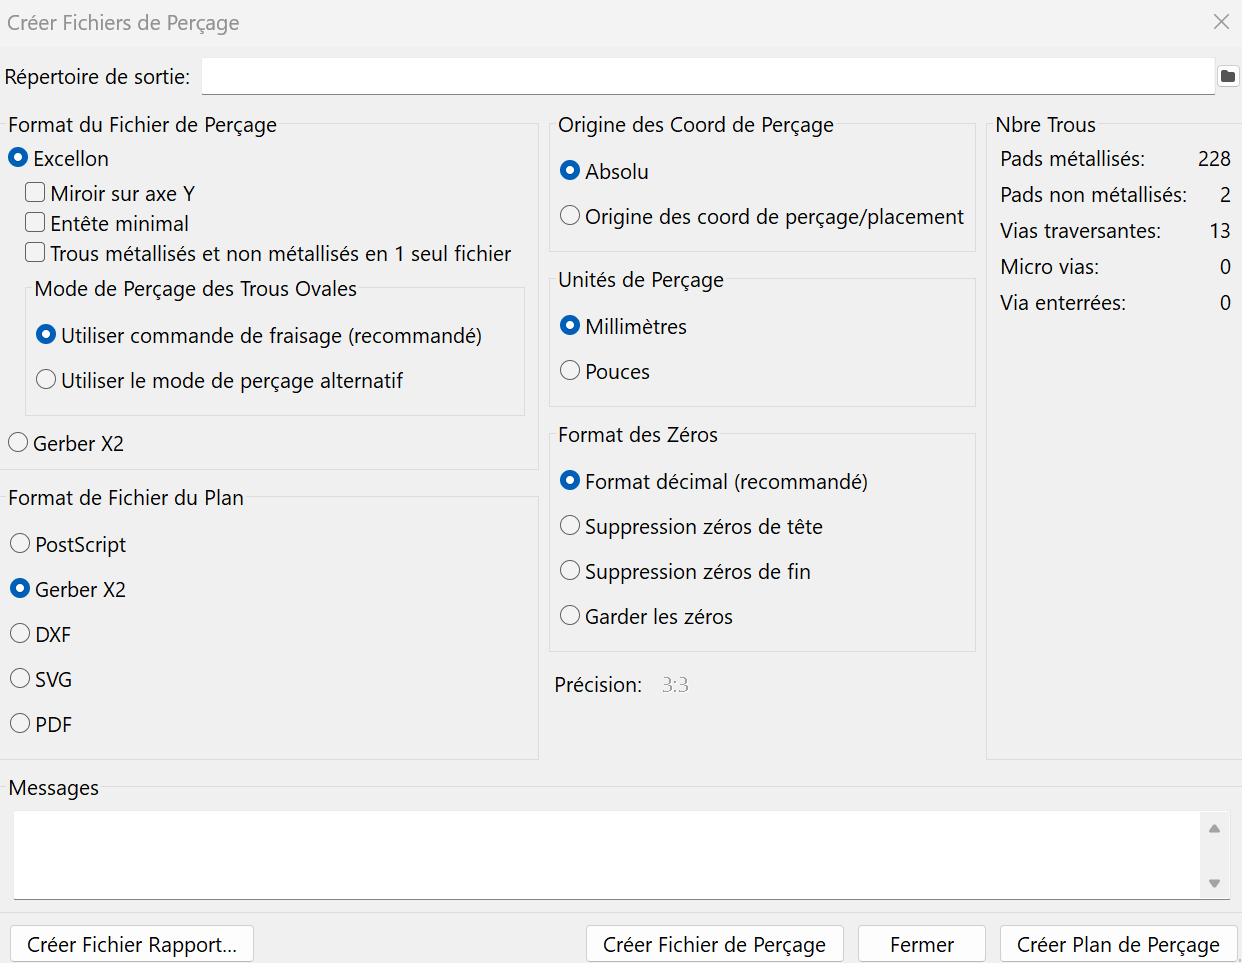
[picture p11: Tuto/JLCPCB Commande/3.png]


Il est recommandé d'utiliser le format Excellon, et le format Gerber X2 comme sur la figure. Cliquer ensuite sur Créer Fichier de Perçage. Une fois tout les fichiers crées, ils apparaîtront dans le répertoire du projet. Il faut maintenant les compresser dans `.zip`.

### Fichiers de position
Il faut ensuite générer un fichier qui indiquera la position de chaque composant. Poiur cela, cliquer sur *Fichier>Fichiers de Fabrication>Placement des Composants*
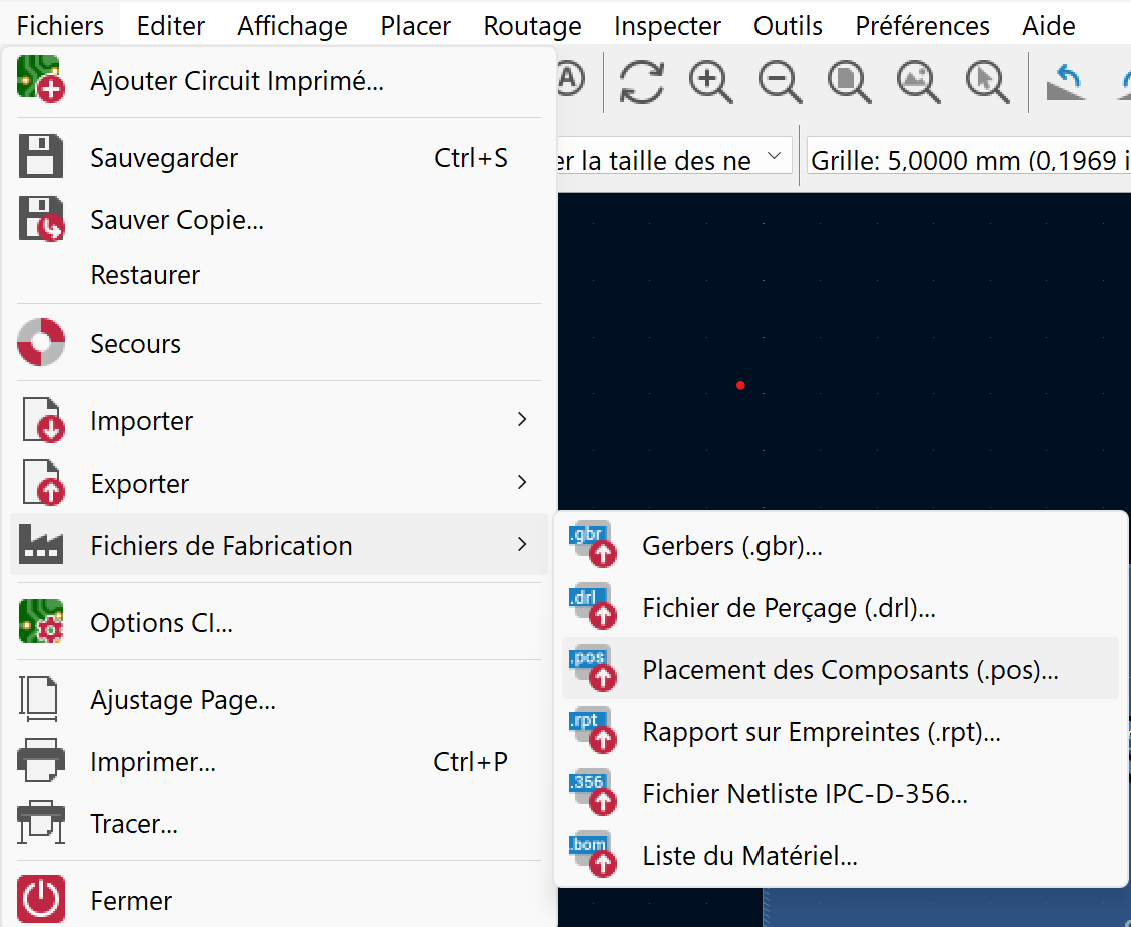
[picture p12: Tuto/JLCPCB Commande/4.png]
 

 Il est préférable de générer un fichier pour le **top** et pour le **bottom**, au format `.csv`. Les deux fichiers seront crées dans le répertoire du projet. Il faut à présent les éditer pour changer les entêtes. 
 - *Ref* devient *Designator*
 - *PosX* devient *Mid X*
 - *PosY* devient *Mid Y*
 - *Rot* devient *Rotation*
 - *Side* devient *Layer*

Ces entêtes sont celles qui seront reconnues par le site de JLCPCB. Le fichier par défaut fournit par KiCAD ne sera pas accepté.

### Bill Of Materials (BOM)

Il faut aussi générer ou créer un fichier BOM qui comprendra :
- Un commentaire (la valeur du composant notamment)
- Les références sur le PCB (R1, C2, U6...)
- Le type d'empreinte utilisée
- La référence du composant sur le site JLCPCB (pas obligatoire mais fortement recommandée)

Le fichier BOM devrait ressembler à ça :

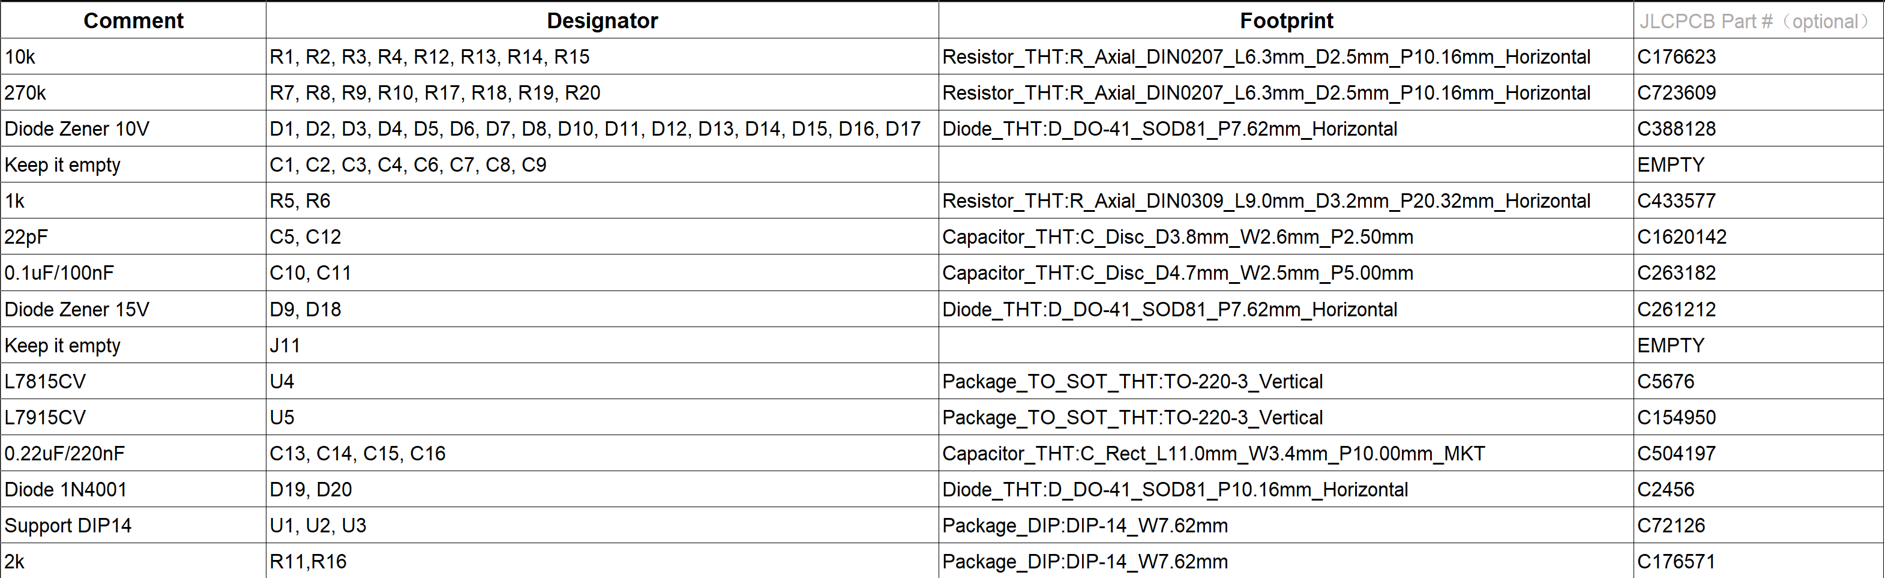
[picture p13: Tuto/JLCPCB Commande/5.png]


Si on veut laisser des emplacements vide sur le PCB, on peut lui indiquer en laissant la ligne vide. J'ai personnellement laisser le fait de laisser vide en commentaire.

## Commande sur le site

Une fois sur le site de JLCPCB, on dépose le dossier `.zip` dans la case de dépôt.

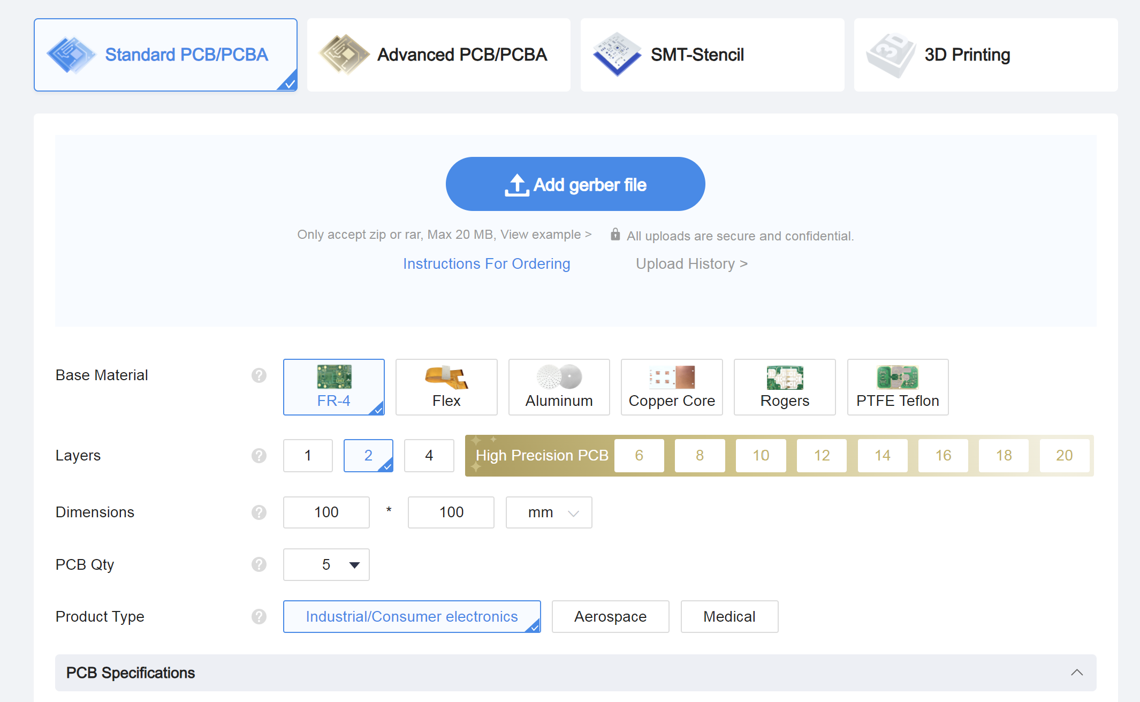
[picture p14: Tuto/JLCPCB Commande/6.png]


On choisit ensuite plusieurs paramètres tels que le nombre de cartes, l'épaisseur, la couleur...

Je recommande de cocher la case **Confirm production file**. De ce fait, un membre de JLCPCB vous contactera par mail afin que vous confirmiez son fichier de production, pour être sûr.

Je recommande aussi de cocher la case **Confirm Part Placement** dans la partie **PCB Assembly**. Comme il peut y avoir des problèmes entre les empreintes KiCAD et celles sur JLCPCB, il faut mieux être sûr que tout les composants soient bien placés.

On ajoute ensuite le fichier BOM et le CPL. Une fenêtre apparaît ensuite avec la liste des composants selectionnés pour les différentes références. Si jamais le site est en manque de stock sur une référence, il faut chercher une alternative dans leur librairie de composant.

On arrive enfin sur la partie placement des composants. Il y a de gros problèmes de compatibilité entre le placement des composants par KiCAD et JLCPCB. De ce fait, il peut arriver que les composants ne soient pas placés aux endroits prévus. Si c'est le cas, vous pouvez tous les replacer à la main directement sur leur site, sinon voir le tutoriel JLC2KICAD pour mettre à jour vos empreintes.

Une fois que le placement des composants correspond à ce que vous vouliez, vous pouvez confirmer la commande.

# Tutorial for ordering on JLCPCB with a KiCAD PCB (EN)

## KiCAD files
### Manufacturing files
To manufacture the PCB on JLCPCB, you need to create Gerber `.gbr` files for the layers you want to create. To do this, in the KiCAD PCB editor, click on *File>Manufacture Files>Gerbers* as shown in the figure below.



A window opens, where you can select the layers to be created. It is essential to keep the layers 

- F.Cu, the top copper layer
- B.Cu, the bottom copper layer
- F.Silkscreen, the top silkscreen layer
- B.Silkscreen is the lower screen print
- F.Mask, the upper solder mask
- B.Mask, the lower mask
- Edge.Cuts, for the edges of the card
  
You can put in all the layers for safety, but some are not necessary, like User.Eco1 for example. Above all, don't forget the mask layers, otherwise the manufacturer won't be able to produce the card



Then click on draw, and you can create the drilling files at the same time (bottom right).



We recommend using the Excellon format, and the Gerber X2 format as shown in the figure. Then click on Create Drilling File. Once all the files have been created, they will appear in the project directory. They now need to be compressed into `.zip'.

### Position files
Next, you need to generate a file indicating the position of each component. To do this, click on *File>Manufacture Files>Component Positioning*.
 

 It is best to generate a file for the **top** and for the **bottom**, in `.csv` format. The two files will be created in the project directory. You now need to edit them to change the headers. 
 - *Ref* becomes *Designator*.
 - PosX* becomes *Mid X*.
 - PosY* becomes Mid Y*.
 - Rot* becomes Rotation
 - *Side* becomes *Layer*

These headers are the ones that will be recognised by the JLCPCB site. The default file provided by KiCAD will not be accepted.

### Bill Of Materials (BOM)

You also need to generate or create a BOM file which will include :
- A comment (the value of the component in particular)
- PCB references (R1, C2, U6, etc.)
- The type of footprint used
- The component reference on the JLCPCB site (not compulsory but strongly recommended)

The BOM file should look like this:



If you want to leave empty slots on the PCB, you can indicate this by leaving the line empty. I've personally left it blank as a comment.

## Ordering on the site

Once you're on the JLCPCB site, drop the `.zip` folder in the drop box.



You then choose several parameters such as the number of cards, thickness, colour, etc.

I recommend ticking the **Confirm production file** box. This way, a JLCPCB member will contact you by email to confirm their production file, just to be sure.

I also recommend checking the **Confirm Part Placement** box in the **PCB Assembly** section. As there can be problems between the KiCAD footprints and those on JLCPCB, it's best to be sure that all the components are correctly placed.

We then add the BOM file and the CPL. A window then appears with the list of components selected for the different references. If the site is ever out of stock on a part number, you need to look for an alternative in their component library.

Finally, we come to the component placement section. There are major compatibility problems between the placement of components by KiCAD and JLCPCB. As a result, components may not be placed where they should be. If this is the case, you can replace them all by hand directly on their site, otherwise see the JLC2KICAD tutorial to update your footprints.

Once the placement of the components matches what you wanted, you can confirm the order.

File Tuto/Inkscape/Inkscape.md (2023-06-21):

# Tutoriel Gravure InkScape (FR)

## Contexte
Les plaques d'aluminium sont noires par défaut. On cherche à enlever toute la partie noir sauf aux endroits ou l'on souhaite faire apparaître des inscriptions. C'est un procédé un peu inverse à la gravure habituelle. Comme on cherche à faire l'inverse, la méthode utilisée est un peu différente.

## Préparation

Afin de pouvoir créer un fichier `.svg` pour la gravure laser, il faut d'abord préparer quelques chose. 
Dans un premier temps, un rectangle **rempli** d'une certaine couleur, de la dimension d'une plaque d'aluminium. Ces plaques font environ 128,5mm par 62 mm. Vous pouvez aussi utiliser le template disponible dans le dossier **Gravure**.

Avec une autre couleur, créer les éléments que vous voulez graver. Cela peut être du texte, des formes, ou autre. Une fois ces éléments créer, il faut les placer sur le rectangle comme vous voudriez que ce  soit graver.

## Outil différence
Le principe est donc de "soustraire" les formes que l'on veut graver au rectangle de départ. Pour ce faire on sélectionne d'abord la forme que l'on souhaite graver, puis le rectangle de départ en appuyant sur `'Ctrl'+'Shift'` pour faire une séléction multiple. une fois que les deux éléments sont sélectionnés, appuyer sur `'Ctrl'+'-'` pour faire la différence entre les deux objets.

Le rectangle de départ sera donc "creusé" par cette forme. Il faut ensuite répéter l'opération pour toutes les formes que l'on souhaite graver. J'ai remarqué qu'on ne peut pas faire une sélection multiple de textes pour ensuite les soustraire.

A la fin, il ne devrait vous rester qu'une seule forme : le rectangle creusé.

# InkScape Engraving Tutorial (EN)

## Background
Aluminium plates are black by default. We want to remove all the black except where we want the inscriptions to appear. It's the opposite of the usual engraving process. As we are trying to do the opposite, the method used is a little different.

## Preparation

In order to create an `.svg' file for laser engraving, you first need to prepare a few things. 
Firstly, a rectangle **filled** with a certain colour, the size of an aluminium plate. These plates are approximately 128.5 mm by 62 mm. You can also use the template available in the **Engraving** folder.

Using another colour, create the elements you want to engrave. This could be text, shapes or anything else. Once you have created these elements, place them on the rectangle as you would like them to be engraved.

## Difference tool
The principle is to 'subtract' the shapes you want to engrave from the starting rectangle. To do this, first select the shape you want to engrave, then the starting rectangle by pressing `'Ctrl'+'Shift'` to make a multiple selection. Once the two elements are selected, press `'Ctrl'+'-'` to make the difference between the two objects.

The starting rectangle will then be 'hollowed out' by this shape. You then need to repeat the operation for all the shapes you want to engrave. I noticed that you can't make a multiple selection of texts and then subtract them.

In the end, you should be left with just one shape: the hollowed-out rectangle.

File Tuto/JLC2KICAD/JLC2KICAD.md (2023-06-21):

# Tutoriel pour utiliser JLC2KiCad (FR)

## Introduction

JLC2KiCad est un outil développé en **Python** qui permet, à l'aide de la référence JLCPCB, de générer un fichier symbole `.sym`, un fichier empreinte `.mod` et un fichier de modèle 3d `.wrl`. 

## Pré-requis

Afin de pouvoir utiliser JLC2KiCad, il faut au préalable :

1. Posséder une version de Python supérieure à la version 3.6
2. Avoir ajouter Python dans les variables globales Windows

Normalement, Python est présent dans les variables globales car il le propose à l'installation. Si jamais la commande `pip` n'est pas reconnue, c'est que la variable globale est manquante. Pour l'ajouter, se rendre dans *Propriétés systèmes>Variables d'environnement*. Dans la catégorie *Variables utilisateurs*, celle du dessus, on doit trouver la variable *Path*. Cliquer sur modifier et ajouter le chemin vers l'installation de Python.

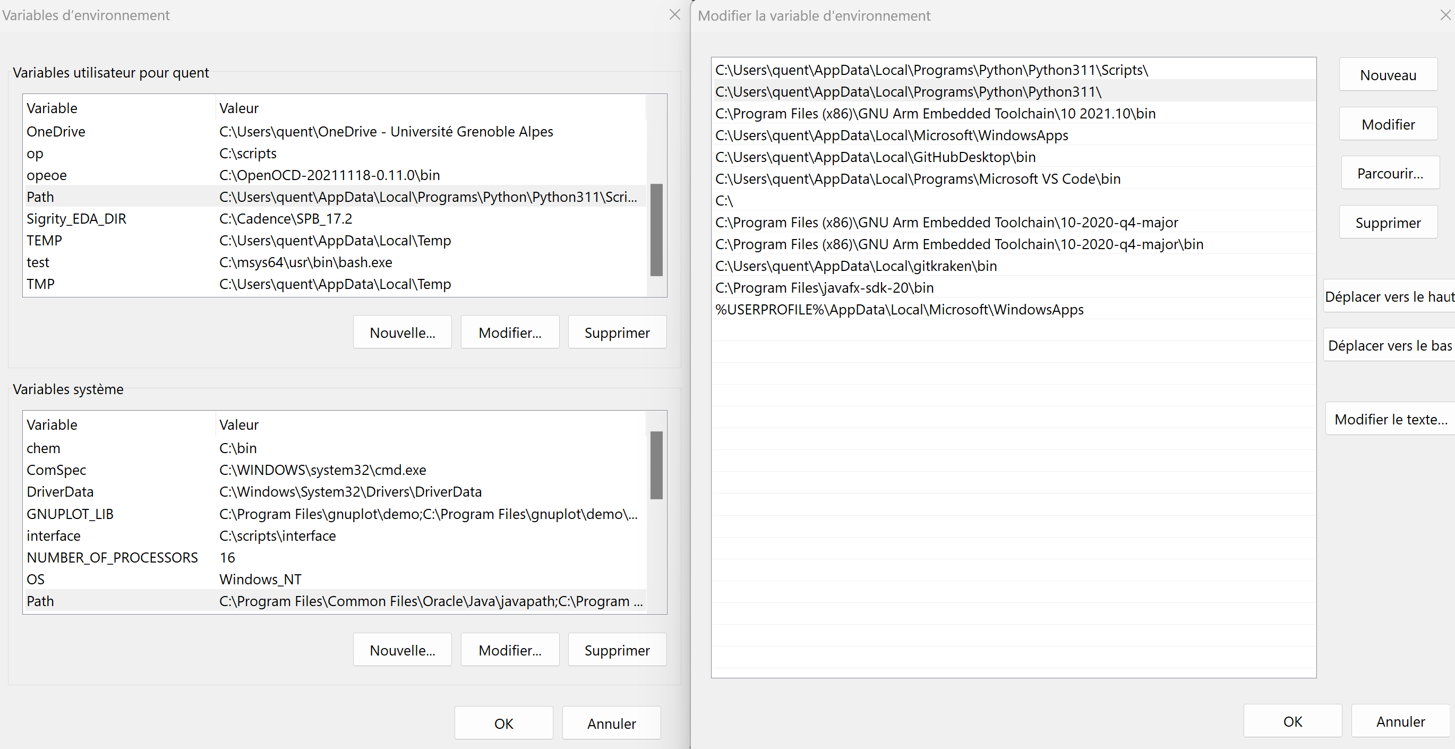
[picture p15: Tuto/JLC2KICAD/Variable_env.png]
Image indisponible Variables d'environnement Windows


## Installation
Pour installer l'application, lancer une invite de commande Windows, et taper `pip install JLC2KiCadLib`. Si l'erreur est que pip n'est pas reconnue, veuillez vous reporter au pré-requis.

## Utilisation

A présent, vous pouvez créer ou choisir un dossier dans lequel seront stockées vos fichiers KiCAD. Une fois cela fait, prenez une ou des références de composants JLCPCB. Elle peuvent être trouvées dans le champ **JLCPCB Part #** sur le site internet de JLCPCB. Ensuite, exécuter la ligne suivante :

`JLC2KiCadLib -dir CHEMINDUDOSSIER --skip_existing PARTNUMBER`

Avec CHEMINDUDOSSIER le chemin du dossier dans lequel les fichiers seront stockés et PARTNUMBER la/les références de composants JLCPCB. Ils peuvent être mis à la suite avec un espace en guise de séparation.

## Exemple

Je cherche à stocker dans un dossier nommé KICAD sur mon Bureau les fichiers de toute ma liste de composants. La ligne sera la suivante :

`JLC2KiCadLib -dir C:\Users\quent\Desktop\KICAD --skip_existing C176623 C72126 C176571 C2456 C388128 C154950 C263182 C261212 C504197 C433577 C1620142 C723609`

Ce qui me génerera les 3 fichiers (symbole, empreinte et modèle 3d) dans le dossier KICAD pour tout les composants cités.

## Options

Pour certaines raisons, il se peut que vous ne souhaitiez pas certains fichiers.
- `--no footprint` permet de ne pas générer d'empreintes
- `--no symbol` permet de ne pas générer de symboles
- `-symbol_lib SYMBOL_LIB` permet de chosir le nom de la librairie de symbole, en remplaçant SYMBOL_LIB par le nom souhaité
- `-footprint_lib FOOTPRINT_LIB` permet de choisir le nom de la librairie d'empreintes, en remplaçant FOOTPRINT_LIB par le nom souhaité

# Tutorial for using JLC2KiCad (EN)

## Introduction

JLC2KiCad is a **Python** tool which allow you, thanks to the JLCPCB part number, to create a symbol file `.sym`, a footprint file `.mod` and a 3D model file `.wrl`. 

## Prerequisites

In order to use JLC2KiCad, you must first :

1. Have a Python version higher than 3.6
2. Add Python to Windows global variables

Normally, Python is present in the global variables because it is proposed during installation. If the `pip` command is not recognized, the global variable is missing. To add it, go to *System properties>Environment variables*. In the *User variables* category, the one above, you should find the *Path* variable. Click on modify and add the path to the Python installation.

Image indisponible Variables d'environnement Windows

## Installation
To install the application, launch a Windows command prompt, and type `pip install JLC2KiCadLib`. If the error is that pip is not recognized, please refer to the prerequisites.

## Application

Now you can create a folder in which to store your KiCAD files. Once this has been done, select one or more JLCPCB part numbers. These can be found in the **JLCPCB Part #** field. Then execute the following line:

`JLC2KiCadLib -dir REPOPATH --skip_existing PARTNUMBER`

With REPOPATH the path of the folder in which the files will be stored and PARTNUMBER the JLCPCB component reference(s). They can be placed one after the other, separated by a space.

## Example

I want to store the files for my entire list of components in a folder called KICAD on my desktop. The line will be as follows:

`JLC2KiCadLib -dir C:\Users\quent\Desktop\KICAD --skip_existing C176623 C72126 C176571 C2456 C388128 C154950 C263182 C261212 C504197 C433577 C1620142 C723609`

This will generate the 3 files (symbol, footprint and 3d model) in the KICAD folder for all the components mentioned.

## Options

For certain reasons, you may not wish to generate certain files.
- `--no footprint` allows you not to generate footprints
- `--no symbol` means no symbol generation
- `-symbol_lib SYMBOL_LIB` allows you to select the name of the symbol library, replacing SYMBOL_LIB with the desired name
- `--footprint_lib FOOTPRINT_LIB` selects the name of the footprint library, replacing FOOTPRINT_LIB with the desired name

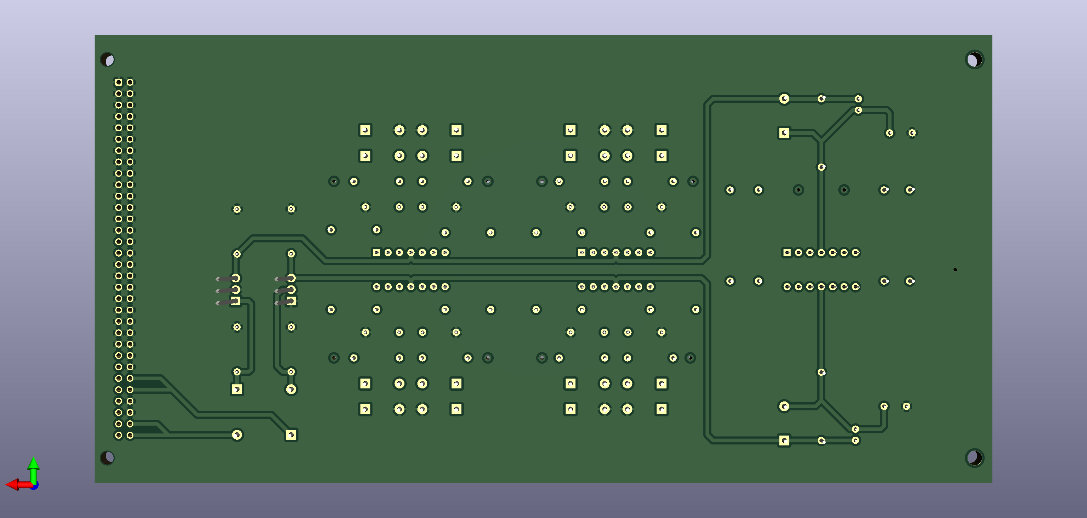
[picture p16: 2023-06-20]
Documentation PCB/Images/pcb_3d_bottom.png

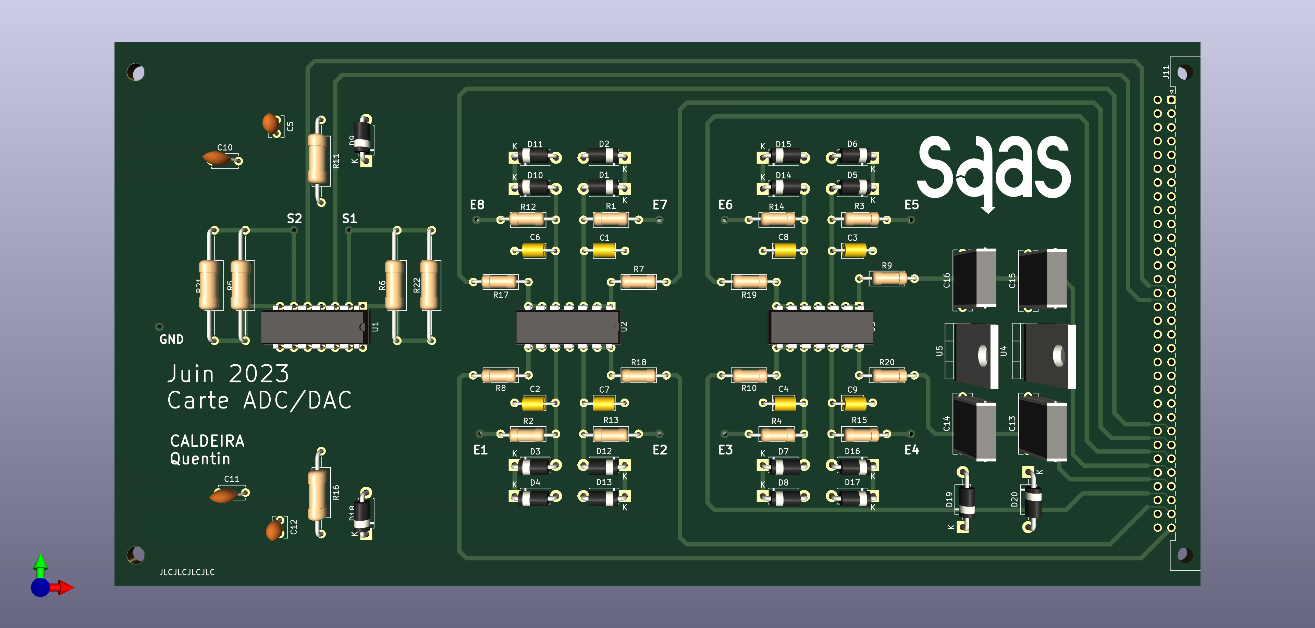
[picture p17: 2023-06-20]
Documentation PCB/Images/pcb_3d_top.png

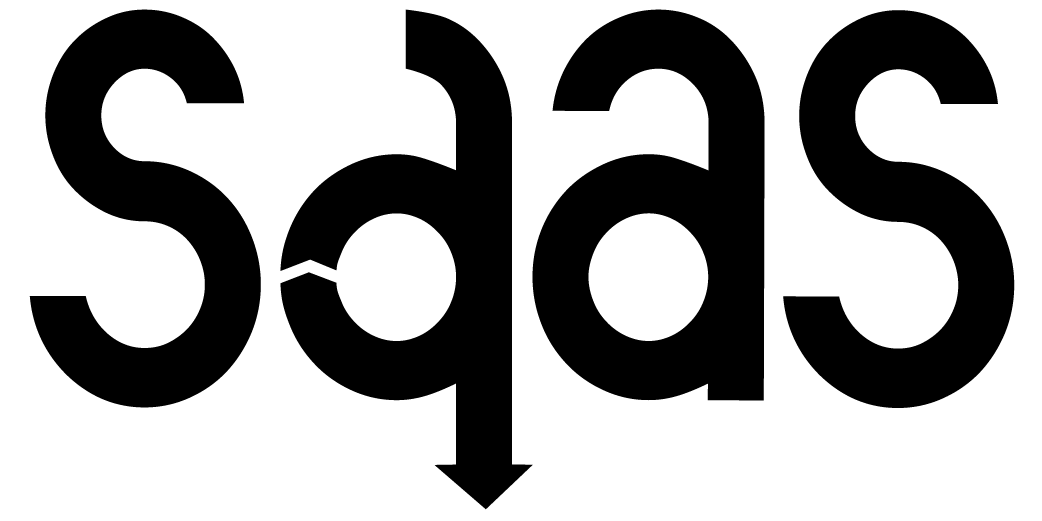
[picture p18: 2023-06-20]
LaTeX/SAAS.png

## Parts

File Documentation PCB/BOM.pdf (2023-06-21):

Comment | Designator
10k | R1, R2, R3, R4, R12, R13, R14, R15
270k | R7, R8, R9, R10, R17, R18, R19, R20
Diode Zener 10V | D1, D2, D3, D4, D5, D6, D7, D8, D10, D11, D12, D13, D14, D15, D16, D17
Keep it empty | C1, C2, C3, C4, C6, C7, C8, C9
1k | R5, R6
22pF | C5, C12
0.1uF/100nF | C10, C11
Diode Zener 15V | D9, D18
Keep it empty | J11
L7815CV | U4
L7915CV | U5
0.22uF/220nF | C13, C14, C15, C16
Diode 1N4001 | D19, D20
Support DIP14 | U1, U2, U3
10k | R11,R16

Footprint | JLCPCB Part #（optional）
Resistor_THT:R_Axial_DIN0207_L6.3mm_D2.5mm_P10.16mm_Horizontal | C176623
Resistor_THT:R_Axial_DIN0207_L6.3mm_D2.5mm_P10.16mm_Horizontal | C723609
Diode_THT:D_DO-41_SOD81_P7.62mm_Horizontal | C388128
| EMPTY
Resistor_THT:R_Axial_DIN0309_L9.0mm_D3.2mm_P20.32mm_Horizontal | C433577
Capacitor_THT:C_Disc_D3.8mm_W2.6mm_P2.50mm | C1620142
Capacitor_THT:C_Disc_D4.7mm_W2.5mm_P5.00mm | C263182
Diode_THT:D_DO-41_SOD81_P7.62mm_Horizontal | C261212
| EMPTY
Package_TO_SOT_THT:TO-220-3_Vertical | C5676
Package_TO_SOT_THT:TO-220-3_Vertical | C154950
Capacitor_THT:C_Rect_L11.0mm_W3.4mm_P10.00mm_MKT | C504197
Diode_THT:D_DO-41_SOD81_P10.16mm_Horizontal | C2456
Package_DIP:DIP-14_W7.62mm | C72126
Package_DIP:DIP-14_W7.62mm | C176571

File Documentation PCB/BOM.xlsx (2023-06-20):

Comment | Designator | Footprint | JLCPCB Part #（optional）
10k | R1, R2, R3, R4, R12, R13, R14, R15 | Resistor_THT:R_Axial_DIN0207_L6.3mm_D2.5mm_P10.16mm_Horizontal | C176623
270k | R7, R8, R9, R10, R17, R18, R19, R20 | Resistor_THT:R_Axial_DIN0207_L6.3mm_D2.5mm_P10.16mm_Horizontal | C723609
Diode Zener 10V | D1, D2, D3, D4, D5, D6, D7, D8, D10, D11, D12, D13, D14, D15, D16, D17 | Diode_THT:D_DO-41_SOD81_P7.62mm_Horizontal | C388128
Keep it empty | C1, C2, C3, C4, C6, C7, C8, C9 |  | EMPTY
1k | R5, R6 | Resistor_THT:R_Axial_DIN0309_L9.0mm_D3.2mm_P20.32mm_Horizontal | C433577
22pF | C5, C12 | Capacitor_THT:C_Disc_D3.8mm_W2.6mm_P2.50mm | C1620142
0.1uF/100nF | C10, C11 | Capacitor_THT:C_Disc_D4.7mm_W2.5mm_P5.00mm | C263182
Diode Zener 15V | D9, D18 | Diode_THT:D_DO-41_SOD81_P7.62mm_Horizontal | C261212
Keep it empty | J11 |  | EMPTY
L7815CV | U4 | Package_TO_SOT_THT:TO-220-3_Vertical | C5676
L7915CV | U5 | Package_TO_SOT_THT:TO-220-3_Vertical | C154950
0.22uF/220nF | C13, C14, C15, C16 | Capacitor_THT:C_Rect_L11.0mm_W3.4mm_P10.00mm_MKT | C504197
Diode 1N4001 | D19, D20 | Diode_THT:D_DO-41_SOD81_P10.16mm_Horizontal | C2456
Support DIP14 | U1, U2, U3 | Package_DIP:DIP-14_W7.62mm | C72126
10k | R11,R16 | Package_DIP:DIP-14_W7.62mm | C176571

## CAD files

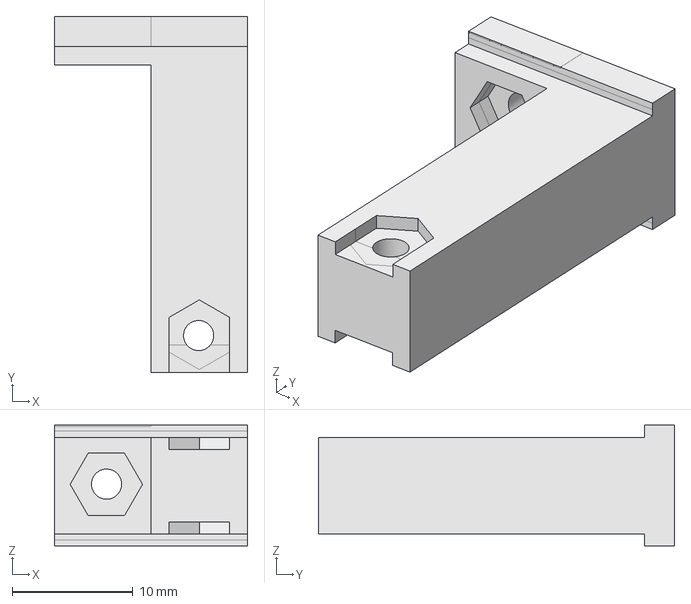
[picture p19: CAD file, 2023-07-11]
3D/model.FCStd
16.0 x 29.5 x 10.0 mm

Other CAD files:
3D/model.stl

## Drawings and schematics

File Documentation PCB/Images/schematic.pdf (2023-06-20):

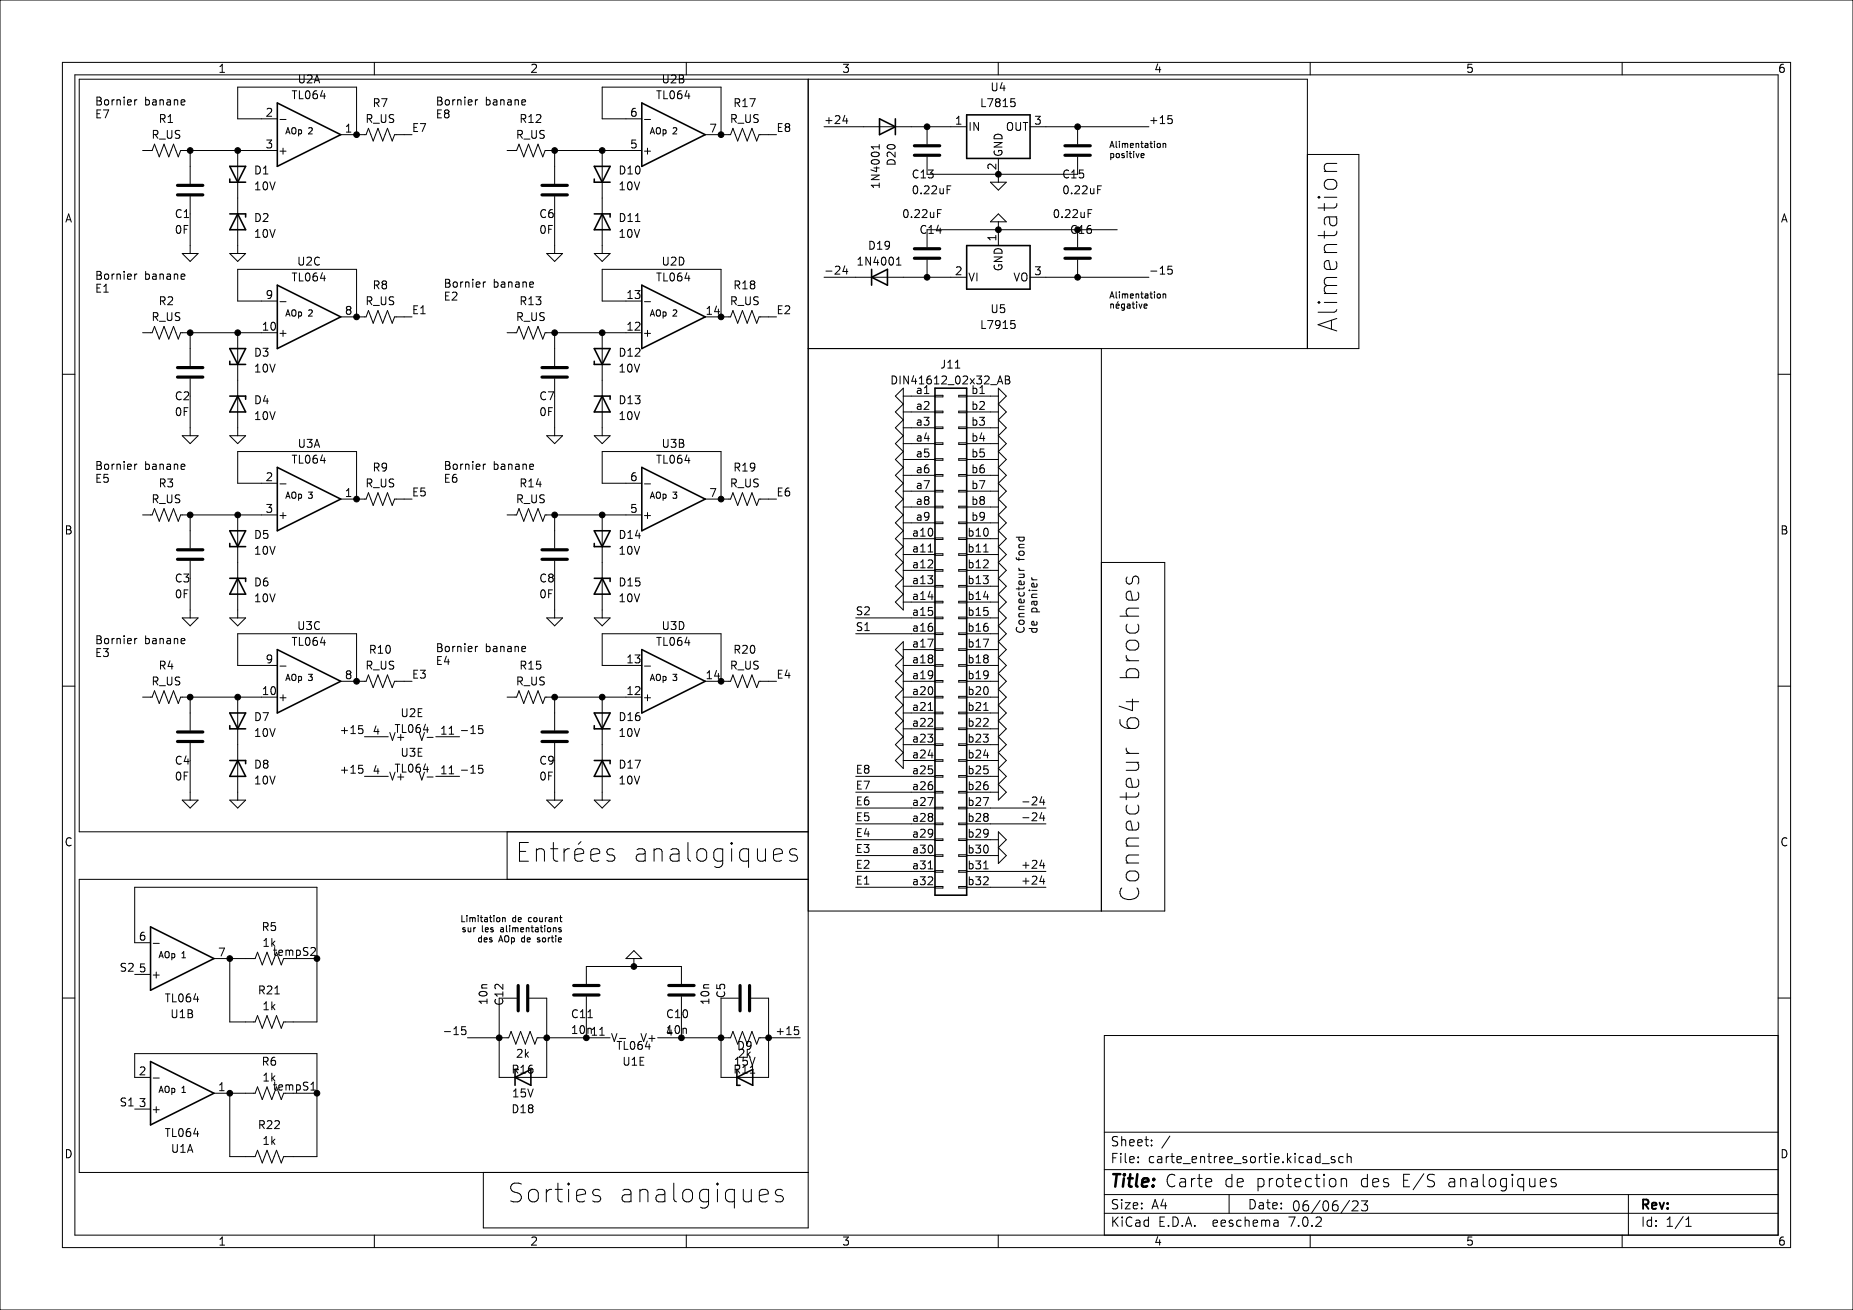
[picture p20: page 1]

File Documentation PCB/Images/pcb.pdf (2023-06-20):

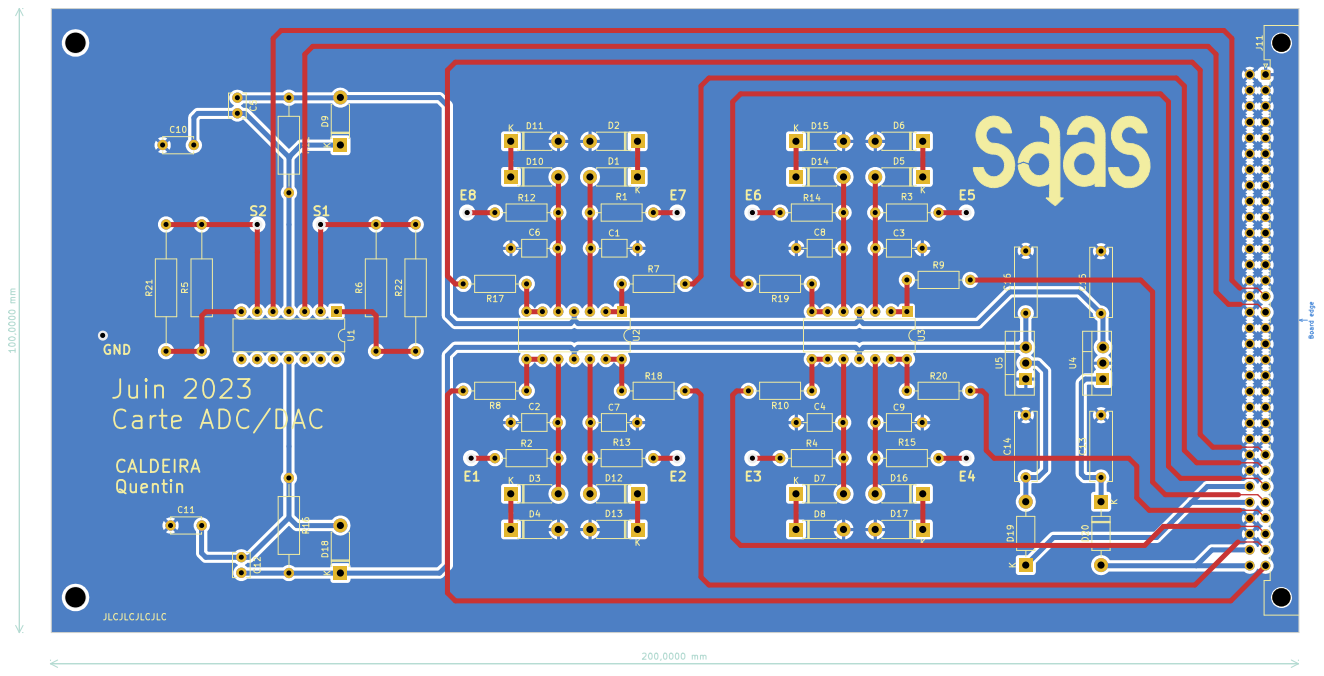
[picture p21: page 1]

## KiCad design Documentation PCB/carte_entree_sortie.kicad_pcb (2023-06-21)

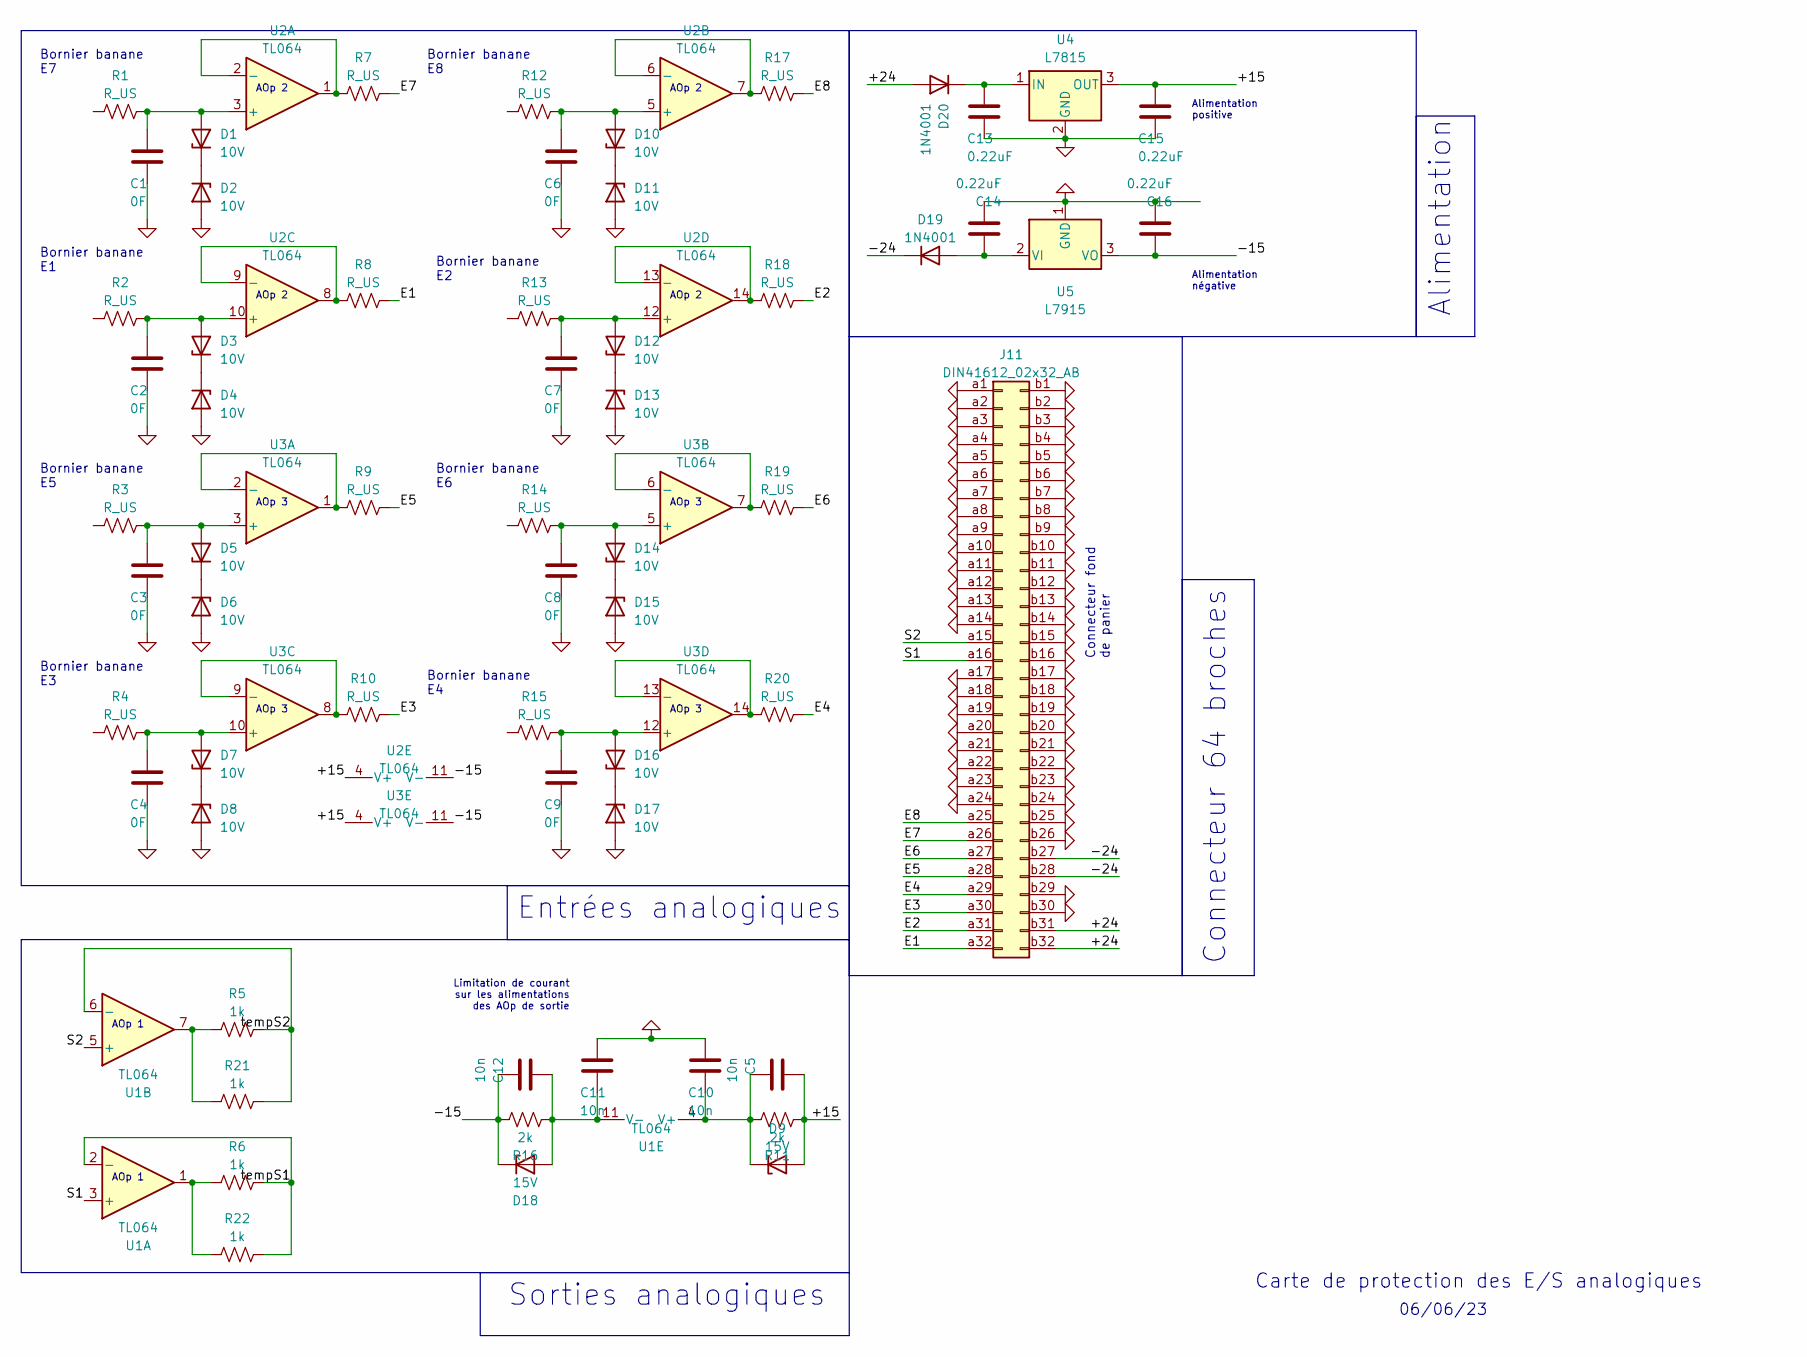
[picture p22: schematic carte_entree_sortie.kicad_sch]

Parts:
C1, C2, C3, C4, C6, C7, C8, C9: 0F; C_Axial_L3.8mm_D2.6mm_P7.50mm_Horizontal
C5, C12: 10n; C_Disc_D3.8mm_W2.6mm_P2.50mm
C10, C11: 10n; C_Disc_D4.7mm_W2.5mm_P5.00mm
C13, C14, C15, C16: 0.22uF; C_Rect_L11.0mm_W3.4mm_P10.00mm_MKT
D1, D2, D3, D4, D5, D6, D7, D8, D10, D11, D12, D13, D14, D15, D16, D17: 10V; D_DO-41_SOD81_P7.62mm_Horizontal
D9, D18: 15V; D_DO-41_SOD81_P7.62mm_Horizontal
D19, D20: 1N4001; D_DO-41_SOD81_P10.16mm_Horizontal
J11: DIN41612_02x32_AB; DIN41612_B_2x32_Male_Horizontal_THT
R1, R2, R3, R4, R7, R8, R9, R10, R12, R13, R14, R15, R17, R18, R19, R20: R_US; R_Axial_DIN0207_L6.3mm_D2.5mm_P10.16mm_Horizontal
R5, R6, R21, R22: 1k; R_Axial_DIN0309_L9.0mm_D3.2mm_P20.32mm_Horizontal
R11, R16: 2k; R_Axial_DIN0309_L9.0mm_D3.2mm_P15.24mm_Horizontal
U1, U2, U3: TL064; DIP-14_W7.62mm
U4: L7815; TO-220-3_Vertical
U5: L7915; TO-220-3_Vertical

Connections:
/+15: C5.1, C15.1, D9.2 (A), R11.1, U2.4 (V+), U3.4 (V+), U4.3 (OUT)
/+24: D20.2 (A), J11.b31, J11.b32
/-15: C12.2, C16.1, D18.1 (K), R16.2, U2.11 (V-), U3.11 (V-), U5.3 (VO)
/-24: D19.1 (K), J11.b27, J11.b28
/E1: J11.a32, R8.2
/E2: J11.a31, R18.2
/E3: J11.a30, R10.2
/E4: J11.a29, R20.2
/E5: J11.a28, R9.2
/E6: J11.a27, R19.2
/E7: J11.a26, R7.2
/E8: J11.a25, R17.2
/S1: J11.a16, U1.3 (+)
/S2: J11.a15, U1.5 (+)
/tempS1: R6.2, R22.2, U1.2 (-)
/tempS2: R5.2, R21.2, U1.6 (-)
GND: C1.2, C2.2, C3.2, C4.2, C6.2, C7.2, C8.2, C9.2, C10.1, C11.1, C13.2, C14.2, C15.2, C16.2, D2.2 (A), D4.2 (A), D6.2 (A), D8.2 (A), D11.2 (A), D13.2 (A), D15.2 (A), D17.2 (A), J11.a1, J11.a2, J11.a3, J11.a4, J11.a5, J11.a6, J11.a7, J11.a8, J11.a9, J11.a10, J11.a11, J11.a12, J11.a13, J11.a14, J11.a17, J11.a18, J11.a19, J11.a20, J11.a21, J11.a22, J11.a23, J11.a24, J11.b1, J11.b2, J11.b3, J11.b4, J11.b5, J11.b6, J11.b7, J11.b8, J11.b9, J11.b10, J11.b11, J11.b12, J11.b13, J11.b14, J11.b15, J11.b16, J11.b17, J11.b18, J11.b19, J11.b20, J11.b21, J11.b22, J11.b23, J11.b24, J11.b25, J11.b26, J11.b29, J11.b30, U4.2 (GND), U5.1 (GND)
unnamed: C1.1, D1.2 (A), R1.2, U2.3 (+)
unnamed: D1.1 (K), D2.1 (K)
unnamed: C2.1, D3.2 (A), R2.2, U2.10 (+)
unnamed: D3.1 (K), D4.1 (K)
unnamed: C3.1, D5.2 (A), R3.2, U3.3 (+)
unnamed: D5.1 (K), D6.1 (K)
unnamed: C4.1, D7.2 (A), R4.2, U3.10 (+)
unnamed: D7.1 (K), D8.1 (K)
unnamed: C5.2, C10.2, D9.1 (K), R11.2, U1.4 (V+)
unnamed: C6.1, D10.2 (A), R12.2, U2.5 (+)
unnamed: D10.1 (K), D11.1 (K)
unnamed: C7.1, D12.2 (A), R13.2, U2.12 (+)
unnamed: D12.1 (K), D13.1 (K)
unnamed: C8.1, D14.2 (A), R14.2, U3.5 (+)
unnamed: D14.1 (K), D15.1 (K)
unnamed: C9.1, D16.2 (A), R15.2, U3.12 (+)
unnamed: D16.1 (K), D17.1 (K)
unnamed: C11.2, C12.1, D18.2 (A), R16.1, U1.11 (V-)
unnamed: C14.1, D19.2 (A), U5.2 (VI)
unnamed: C13.1, D20.1 (K), U4.1 (IN)
unnamed: R5.1, R21.1, U1.7
unnamed: R6.1, R22.1, U1.1
unnamed: R7.1, U2.1, U2.2 (-)
unnamed: R17.1, U2.6 (-), U2.7
unnamed: R8.1, U2.8, U2.9 (-)
unnamed: R18.1, U2.13 (-), U2.14
unnamed: R9.1, U3.1, U3.2 (-)
unnamed: R19.1, U3.6 (-), U3.7
unnamed: R10.1, U3.8, U3.9 (-)
unnamed: R20.1, U3.13 (-), U3.14

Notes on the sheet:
06/06/23
Bornier banane E5
Bornier banane E2
AOp 1
AOp 2
AOp 3
Alimentation positive
Bornier banane E4
Bornier banane E7
Bornier banane E6
Bornier banane E1
Bornier banane E8
Entrées analogiques
Alimentation négative
Carte de protection des E/S analogiques
Connecteur 64 broches
Alimentation
Connecteur fond de panier
Bornier banane E3
Limitation de courant sur les alimentations des AOp de sortie
Sorties analogiques

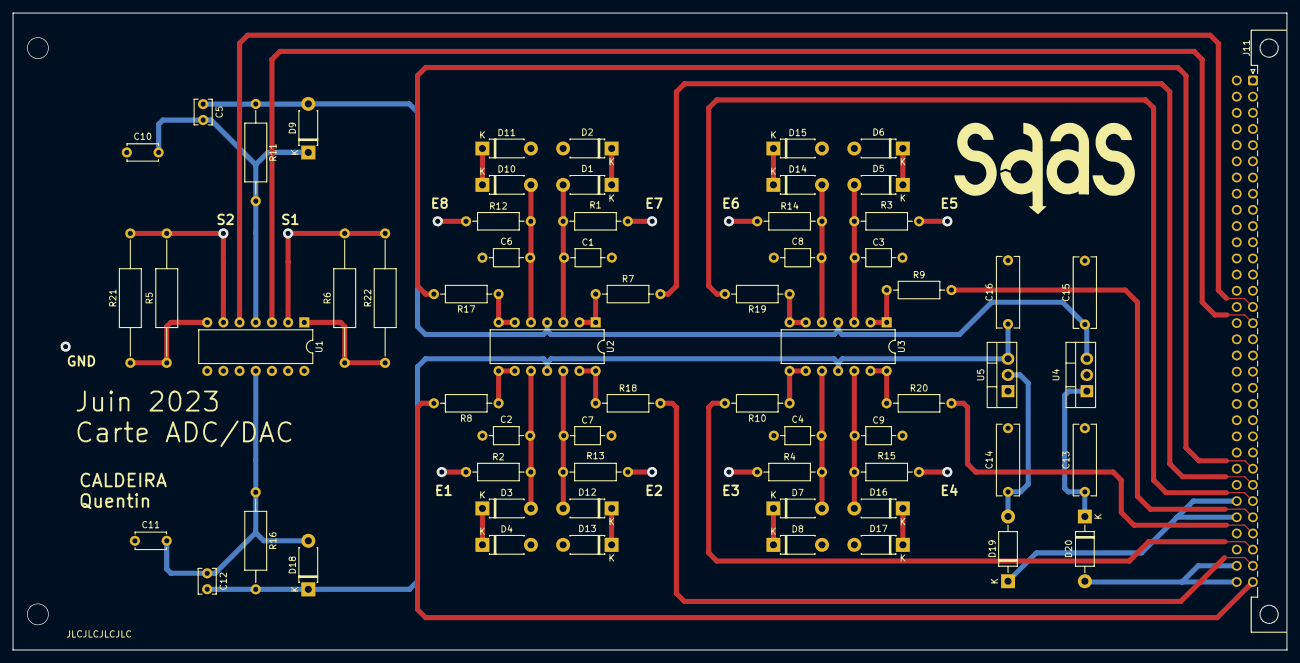
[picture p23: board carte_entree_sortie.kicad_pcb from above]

Board: 2 copper layers, 200.0 x 100.0 mm, 64 parts (0 on the bottom side), 47 nets.

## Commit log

2023-06-20 All files about PCB conception
    [BOM.xlsx, carte_entree_sortie-bottom-pos.csv, carte_entree_sortie-top-pos.csv, carte_entree_sortie.kicad_pcb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]
2023-06-21 Update PCB repo with BOM in pdf
    [carte_entree_sortie.kicad_pcb]
